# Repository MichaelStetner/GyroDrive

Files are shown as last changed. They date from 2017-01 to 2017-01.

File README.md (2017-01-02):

# GyroDrive
Motorized microdrive with integrated gyroscope, accelerometer, and compass

## Connector
The connector is a 7-pin male nano dual row connector from Omnetics (part number A75243-001).

Here is the pinout solder pads, as viewed from above with the connector pins pointing up

```
|                                                                       |
|                              Connector                                |
|                                Body                                   |
|                                                                       |
|                                                                       |
|-----------------------------------------------------------------------|

  |------|  |------|  |------|  |------|  |------|  |------|  |------|
  |      |  |      |  |      |  |      |  |      |  |      |  |      |
  | SCL  |  | SDA  |  |  S1  |  |  S2  |  | +VS  |  | -VS  |  | STIM |
  |      |  |      |  |      |  |      |  |      |  |      |  | OUT  |
  |      |  |      |  |      |  |      |  |      |  |      |  |      |
  |------|  |------|  |------|  |------|  |------|  |------|  |------|

  |------|  |------|  |------|  |------|  |------|  |------|  |------|
  |      |  |      |  |      |  |      |  |      |  |      |  |      |
  | DGND |  |  IX  |  |  S3  |  |  S4  |  | ICOM |  | AGND |  | STIM |
  |      |  |      |  |      |  |      |  |      |  |      |  |  IN  |
  |      |  |      |  |      |  |      |  |      |  |      |  |      |
  |------|  |------|  |------|  |------|  |------|  |------|  |------|
```

Here is the same pinout for the connector pins, as viewed looking head on into the pins with the board on the bottom

```
   /                                                                /
  /                                                                /
 /                                                                /
|----------------------------------------------------------------|
| |------| |------| |------| |------| |------| |------| |------| |
| | STIM | | AGND | | ICOM | |  S4  | |  S3  | |  IX  | | DGND | |
| |  IN  | |      | |      | |      | |      | |      | |      | |
| |------| |------| |------| |------| |------| |------| |------| |
|                                                                |    
| |------| |------| |------| |------| |------| |------| |------| |
| | STIM | | -VS  | | +VS  | |  S2  | |  S1  | | SDA  | | SCL  | |
| | OUT  | |      | |      | |      | |      | |      | |      | |  /
| |------| |------| |------| |------| |------| |------| |------| | /
|----------------------------------------------------------------|/
                            Board side
```

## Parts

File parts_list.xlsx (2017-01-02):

Name on board | Quantity | Purpose | Description | Manufacturer | Part Number | Digikey Link | cart for 1 | http://www.digikey.com/short/3t3hmf | cart for 10 | http://www.digikey.com/short/tn2vvz
X1 | 1 | Omnetics connector | 14 pin nano, male | Omnetics | A75243-001
U1 | 1 | 9 axis inertial measurement unit |  | InvenSense | MPU-9250 | http://www.digikey.com/short/3ttfj7
U2 | 1 | Voltage regulator for digital electronics | 2.5 V linear voltage regulator | Texas Instruments | TPS71525DCKR | http://www.digikey.com/short/3t33f8
U3-U4 | 2 | Instrumentation amplifier |  | Analog Devices | AD8224 | http://www.digikey.com/short/3ttf4f
C1-C2 | 2 | MPU-9250 regulator filter capacitor (C1), VDD bypass capacitor (C2) | 0402, Ceramic, X7R, 0.1uF, 10%, 16V | Murata Electronics | GRM155R71C104KA88D | http://www.digikey.com/short/3ttfv2
C3 | 1 | MPU-9250 VDDIO bypass capacitor | 0201, Ceramic, X7R, 10nF, 10%, 10V | Murata Electronics | GRM033R71A103KA01D | http://www.digikey.com/short/3tt2h3
C4 | 1 | MPU-9250 big bypass capacitor | 0502, Ceramic, X5R, 10uF, 20% 10V | Samsung Electro-Mechanics America, Inc. | CL05A106MP5NUNC | http://www.digikey.com/short/388517
C5 | 1 | Regulator output capacitor | 0402, Ceramic, X5R, 0.47uF, 10%, 6.3V | Murata Electronics | GRM155R60J474KE19D | http://www.digikey.com/short/3t3q8z
C6 | 1 | Regulator input capacitor | 0402, Ceramic, X7R, 0.1uF, 10%, 25V | Murata Electronics | GRM155R71E104KE14D | http://www.digikey.com/short/3t3qcf
C7-C10 | 4 | Bypass capacitor for instrumentation amplifier | 0201, Ceramic, X5R, 0.1uF, 20%, 25V | Murata Electronics | GRM033R61E104ME14D | http://www.digikey.com/short/3t3qrz
C11-C12 | 2 | Big bypass capacitor for instrumentation amplifier | 0603, Ceramic, X5R, 10uF, 20%, 25V | Murata Electronics | GRM188R61E106MA73D | http://www.digikey.com/short/3t3qd2
C13-C17 | 5 | High pass filter for electrodes and virtual ground (with R7-R11) | 0201, Ceramic, X7R, 6800pF, 10%, 16V | TDK Corporation | CGA1A2X7R1C682K030BA | http://www.digikey.com/short/38852m
R1-R2 | 2 | I2C pull-up resistor | 0201, 10kOhm, 1%, 1/20W | Panasonic Electronic Components | ERJ-1GEF1002C | http://www.digikey.com/short/3t3hjp
R3-R6 | 4 | Gain setting resistor for instrumentation amplifier (gain=100) | 0201, 499Ohm, 1%, 1/20W | Panasonic Electronic Components | ERJ-1GEF4990C | http://www.digikey.com/short/3ttm01
R7-R11 | 5 | High pass filter for electrodes and virtual ground (with C13-C17) | 0201, 10MOhm, 1%, 1/20W | Rohm Semiconductor | MCR006YRTF1005 | http://www.digikey.com/short/38853w

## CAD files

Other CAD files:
motorholder_with_motor_and_shuttle-0.skp
motorholder_with_motor_and_shuttle.skp
motorholder_with_motor_and_shuttle2.skp

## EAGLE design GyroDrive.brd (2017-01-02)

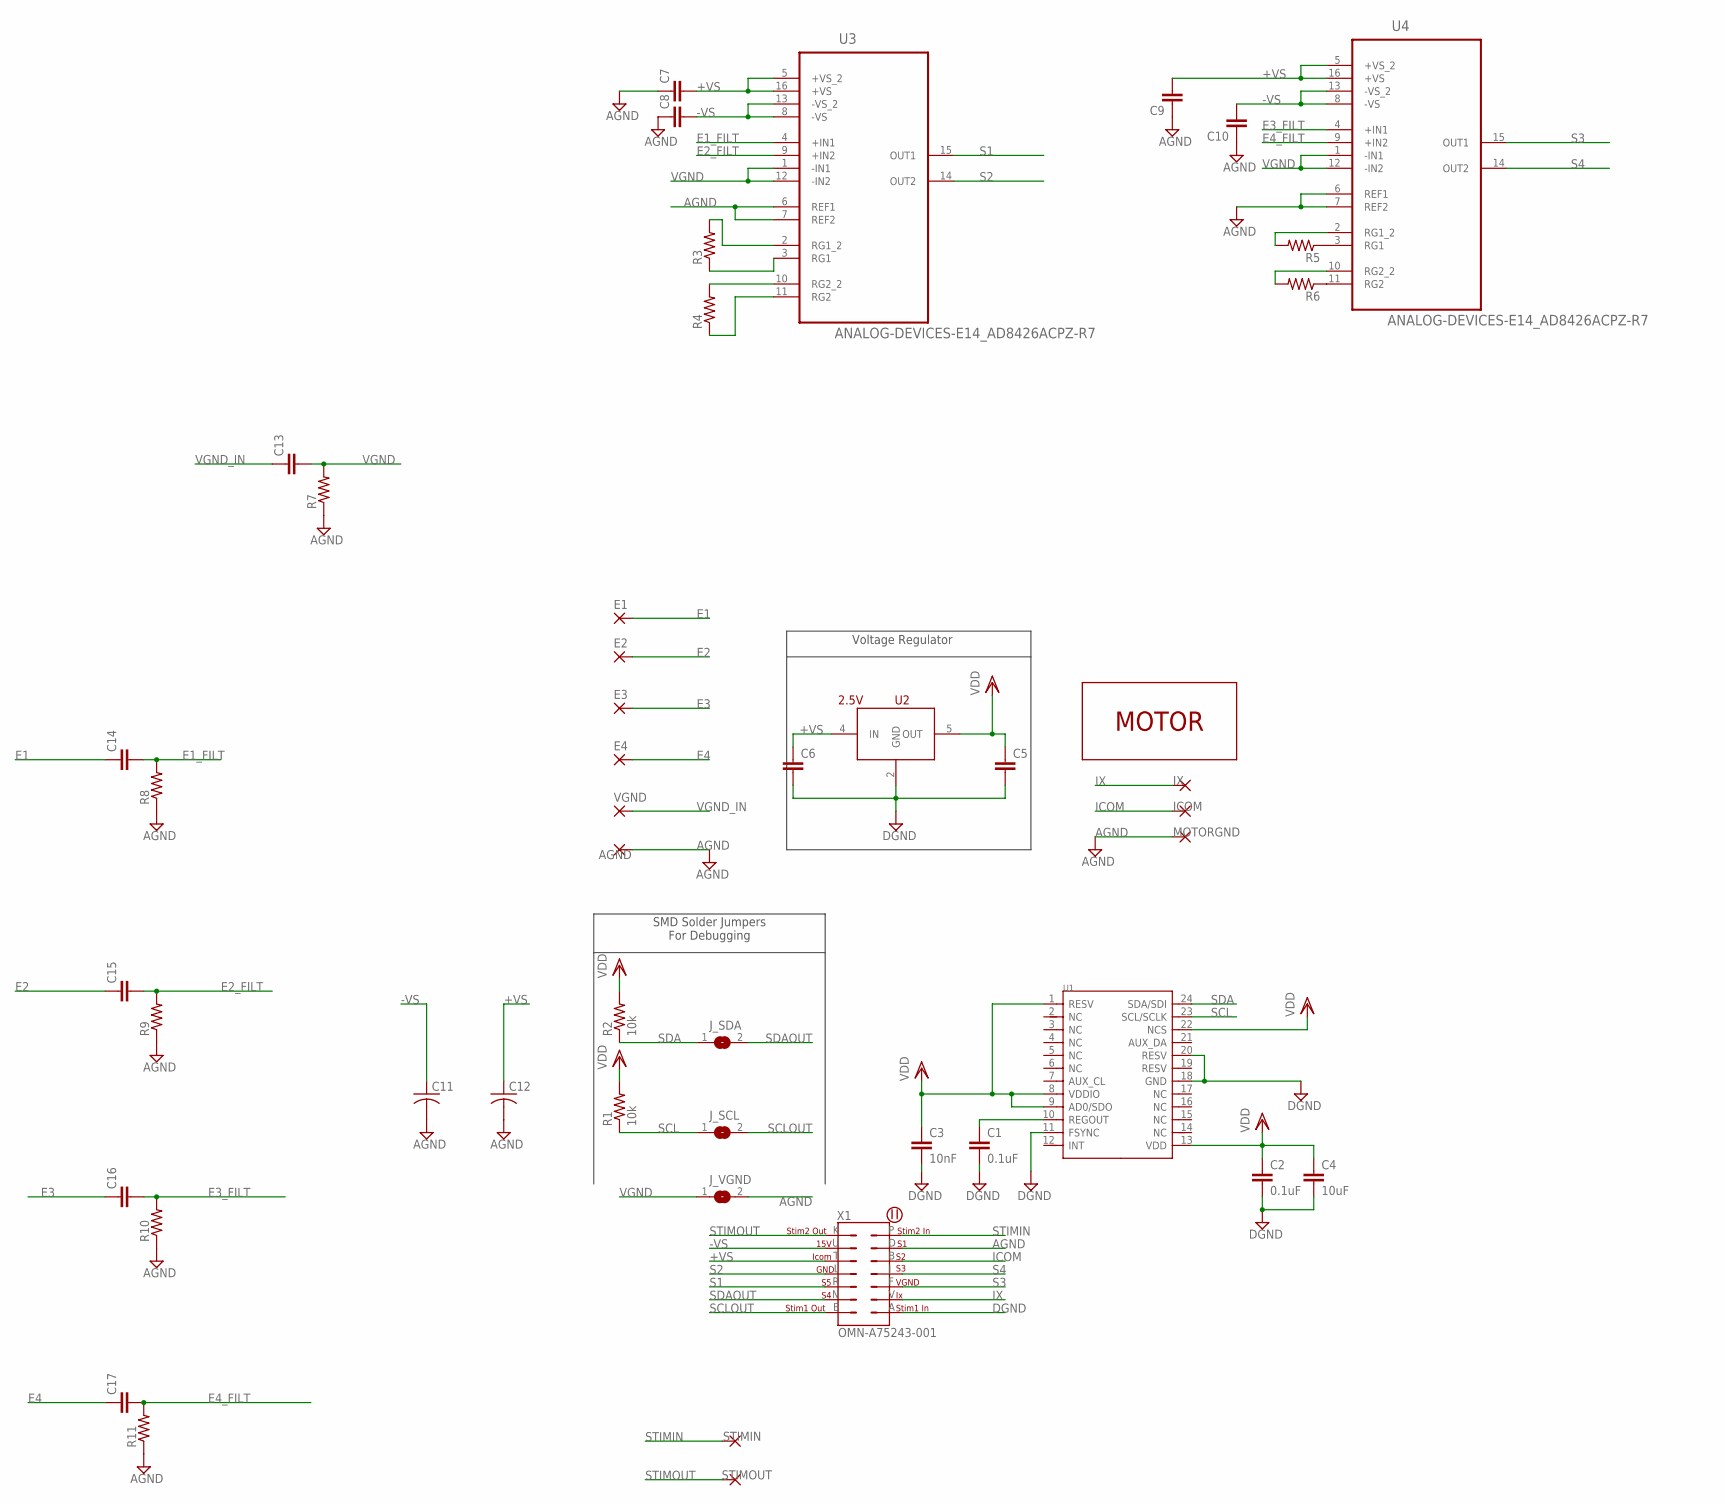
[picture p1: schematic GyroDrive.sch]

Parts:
AGND: THROUGH-HOLE-30MIL/15MIL; 30MIL/15MIL
C1, C2: 0.1uF; C0402
C3: 10nF; C0402
C4: 10uF; C0603
C5, C6: C-EUC0402; C0402
C7, C8, C9, C10, C13, C14, C15, C16, C17: C-EUC0201; C0201
C11, C12: C-USC0603; C0603
E1, E2, E3, E4: SMD25-25-MIL
ICOM: THROUGH-HOLE-30MIL/15MIL; 30MIL/15MIL
IX: THROUGH-HOLE-30MIL/15MIL; 30MIL/15MIL
J_SCL: SJ
J_SDA: SJ
J_VGND: SJ
MOTORGND: THROUGH-HOLE-30MIL/15MIL; 30MIL/15MIL
R1, R2: 10k; R0201
R3, R4, R5, R6, R7, R8, R9, R10, R11: R-US_R0201; R0201
STIMIN: THROUGH-HOLE-30MIL/15MIL; 30MIL/15MIL
STIMOUT: THROUGH-HOLE-30MIL/15MIL; 30MIL/15MIL
U1: MPU-9250; LEAD-QFN24
U2: 2.5V; SC70
U3, U4: ANALOG-DEVICES-E14_AD8426ACPZ-R7; ANALOG-DEVICES-E14_QFN65P400X400X100-16N
U$2: MICRODRIVE-MOTOR; 0206A001B-021-47:1-Y2825
VGND: SMD25-25-MIL
X1: OMN-A75243-001

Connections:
+VS: C6.1, C7.2, C9.2, C12.1, U2.4 (IN), U3.5 (+VS_2), U3.16 (+VS), U4.5 (+VS_2), U4.16 (+VS), X1.T
-VS: C8.2, C10.2, C11.1, U3.8 (-VS), U3.13 (-VS_2), U4.8 (-VS), U4.13 (-VS_2), X1.U
AGND: AGND.P$1, C7.1, C8.1, C9.1, C10.1, C11.2, C12.2, J_VGND.2, MOTORGND.P$1, R7.1, R8.1, R9.1, R10.1, R11.1, U3.6 (REF1), U3.7 (REF2), U4.6 (REF1), U4.7 (REF2), X1.D
DGND: C1.2, C2.2, C3.2, C4.2, C5.2, C6.2, U1.11 (FSYNC), U1.18 (GND), U1.20 (RESV), U2.2 (GND), X1.A
E1: C14.1, E1.1
E1_FILT: C14.2, R8.2, U3.4 (+IN1)
E2: C15.1, E2.1
E2_FILT: C15.2, R9.2, U3.9 (+IN2)
E3: C16.1, E3.1
E3_FILT: C16.2, R10.2, U4.4 (+IN1)
E4: C17.1, E4.1
E4_FILT: C17.2, R11.2, U4.9 (+IN2)
ICOM: ICOM.P$1, X1.B
IX: IX.P$1, X1.V
unnamed: R4.2, U3.10 (RG2_2)
unnamed: C1.1, U1.10 (REGOUT)
unnamed: R4.1, U3.11 (RG2)
unnamed: R3.1, U3.3 (RG1)
unnamed: R3.2, U3.2 (RG1_2)
unnamed: R5.1, U4.3 (RG1)
unnamed: R5.2, U4.2 (RG1_2)
unnamed: R6.2, U4.10 (RG2_2)
unnamed: R6.1, U4.11 (RG2)
S1: U3.15 (OUT1), X1.R
S2: U3.14 (OUT2), X1.L
S3: U4.15 (OUT1), X1.F
S4: U4.14 (OUT2), X1.J
SCL: J_SCL.1, R1.1, U1.23 (SCL/SCLK)
SCLOUT: J_SCL.2, X1.E
SDA: J_SDA.1, R2.1, U1.24 (SDA/SDI)
SDAOUT: J_SDA.2, X1.N
STIMIN: STIMIN.P$1, X1.P
STIMOUT: STIMOUT.P$1, X1.K
VDD: C2.1, C3.1, C4.1, C5.1, R1.2, R2.2, U1.1 (RESV), U1.8 (VDDIO), U1.9 (AD0/SDO), U1.13 (VDD), U1.22 (NCS), U2.5 (OUT)
VGND: C13.2, J_VGND.1, R7.2, U3.1 (-IN1), U3.12 (-IN2), U4.1 (-IN1), U4.12 (-IN2)
VGND_IN: C13.1, VGND.1

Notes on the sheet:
Voltage Regulator
SMD Solder Jumpers For Debugging

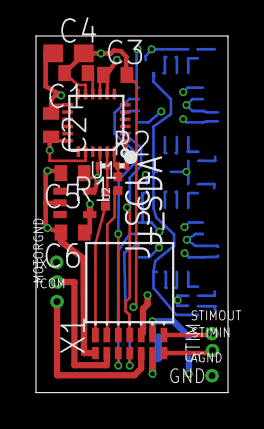
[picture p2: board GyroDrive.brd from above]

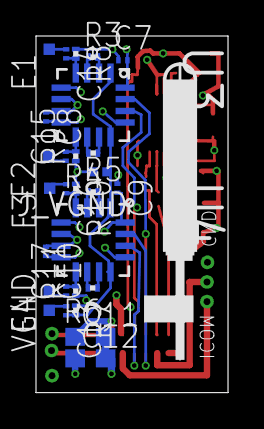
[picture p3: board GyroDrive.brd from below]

Board: 4 copper layers, 10.7 x 19.8 mm, 48 parts (29 on the bottom side), 36 nets.

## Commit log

2015-11-18 Schematic added, based on MicroIMU
    [GyroDrive.brd, GyroDrive.sch]
2015-11-19 Preliminary board layout
    [GyroDrive.brd]
2015-11-19 Preliminary layout with smaller through-holes
    [GyroDrive.brd, GyroDrive.sch]
2015-11-19 Routing in progress. Having trouble with getting electrodes to FETs
    [GyroDrive.brd]
2015-11-19 Routing in progress. FETs done, except VGND. Still need to rout stim and motor.
    [GyroDrive.brd]
2015-11-20 Routing done
    [GyroDrive.brd, GyroDrive.sch]
2015-11-20 In progress - rearrangement to put Omnetics connector lower, per Michale's suggestion
    [GyroDrive.brd]
2015-12-01 Routing finished
    [GyroDrive.brd]
2015-12-01 parts list spreadsheet added
    [parts_list.xlsx]
2015-12-01 Cleaned up routing
    [GyroDrive.brd]
2015-12-01 Added solder jumpers for SDA, SCL, and digital ground
    [GyroDrive.brd, GyroDrive.sch]
2015-12-01 Moved SCL jumper to left of omnetics connector, separated motor ground from ground plane
    [GyroDrive.brd, GyroDrive.sch]
2015-12-01 Bypass capacitor for L3GD20H rewired with more direct connection to 0V supply
    [GyroDrive.brd]
2015-12-02 Silkscreen - added axes labels for gyroscope/accelerometer/magnetometer and also my name, lab, and year
    [GyroDrive.brd]
2015-12-02 Rev 2 submitted to Advanced Circuits for quote. Fixed spacing issues.
    [GyroDrive.brd]
2015-12-03 Changed schematic to make more sense (Rev 3 to Advanced Circuits)
    - Changed input voltage net name from +15V to VCC because VCC can be anything from 2.5V to 30V
    - Separate nets for digital and analog grounds (DGND and GND)
    -- Causes DRC to catch my mistake when digital and analog ground overlap
    - New nets SDAOUT and SCLOUT to represent SDA and SCL after passing through jumper
    -- Stops ratsnest from telling me I have things to do when the two terminals of the jumper are not connected to each other
    -- Pullup resistors moved to SDA and SCL nets (they used to be near omnetics connector on schematic, which put them on SDAOUT and SCLOUT)
    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
    [GyroDrive.brd, GyroDrive.sch]
2015-12-03 Corrected parts list - one of the 0.01 uF capacitors is 0402 size
    [parts_list.xlsx]
2015-12-03 WIP: reroute with no vias or traces under chip
    [GyroDrive.brd]
2016-01-13 Corrected capacitors in parts list
    [parts_list.xlsx]
2016-01-15 Switched to Invensense MPU-9250
    [GyroDrive.brd, GyroDrive.sch]
2016-01-15 Moved motor solder points lower
    [GyroDrive.brd]
2016-01-26 Added instrumentation amplifiers for neural signals
    [GyroDrive.brd, GyroDrive.sch]
2016-01-26 Removed copper from underneath MPU-9250
    [GyroDrive.brd, GyroDrive.sch]
2016-01-26 Added jumper between VGND and AGND
    [GyroDrive.brd, GyroDrive.sch]
2016-01-26 Moved vias to make return paths shorter
    [GyroDrive.brd]
2016-01-26 Added attachment points for a grounding shield
    [GyroDrive.brd, GyroDrive.sch]
2016-01-26 Made board more vertical - moved IMU up, and rotated instrumentation amplifier block by 90 degrees
    [GyroDrive.brd, GyroDrive.sch]
2016-01-27 routing in progress
    [GyroDrive.brd]
2016-01-27 Finished routing digital components
    [GyroDrive.brd, GyroDrive.sch]
2016-01-28 Changed pinout, spaced vias for in-amps to minimum distance that avoids errors
    [GyroDrive.brd, GyroDrive.sch]
2016-01-28 Cleaned up routing around in-amps
    [GyroDrive.brd]
2016-01-28 Switched +VS and -VS on pinout and analog power layer. Finished routing!
    [GyroDrive.brd, GyroDrive.sch]
2016-01-28 Added bypass capacitor for SDA pull-up resistor, shorted SDA and SCL jumpers with traces
    [GyroDrive.brd, GyroDrive.sch]
2016-01-28 Changed pinout to group digital signals closer together
    [GyroDrive.brd, GyroDrive.sch]
2016-01-29 Added high pass filters in front of inputs to in-amps
    [GyroDrive.brd, GyroDrive.sch]
2016-01-29 Added high pass filter for VGND. Attachment point for AGND changed to through hole.
    [GyroDrive.brd, GyroDrive.sch]
2016-02-02 New instrumentation amplifier - AD8224. Old amplifier had too low bandwidth.
    [GyroDrive.brd, GyroDrive.sch, parts_list.xlsx]
2016-02-02 Removed resistor to ground before blocking capacitors
    [GyroDrive.brd, GyroDrive.sch, parts_list.xlsx]
2016-02-02 Instrumentation amplifier changed to AD8224
    [GyroDrive.brd, GyroDrive.sch]
2016-02-02 Incorporated many improvements from the inamp-vertical branch
    [GyroDrive.brd, GyroDrive.sch]
2016-02-02 Improvements suggested by Galen
    - Moved via to get rid of overlap with trace
    - Cleaned up routing
    - Moved S2 via away from corner of amplifier chip
    - Widened power traces
    [GyroDrive.brd]
2016-02-03 Added silk screen (layers 121 and 122)
    [GyroDrive.brd]
2016-02-08 updated libraries - removed pad on bottom of mpu 9250
    [GyroDrive.brd, GyroDrive.sch]
2016-02-09 Updated parts list - added I2C pull up resistors (R10-R11)
    [parts_list.xlsx]
2016-03-29 Updated parts list C4 changed to ceramic type (from tantalum) C13-C17 changed to 6800pF (from 47nF) R7-R11 changed to 10M (from 1.5M)
    [parts_list.xlsx]
2016-04-25 Added motor holder drawing (SketchUp)
    [motorholder_with_motor_and_shuttle.skp]
2016-04-27 updated motor holder
    - support for shuttle lowered by 150 um
    - support for shuttle widened by 50 um
    [motorholder_with_motor_and_shuttle.skp]
2016-05-23 added design for motor holder
    [motorholder_with_motor_and_shuttle-0.skp, motorholder_with_motor_and_shuttle2.skp]
